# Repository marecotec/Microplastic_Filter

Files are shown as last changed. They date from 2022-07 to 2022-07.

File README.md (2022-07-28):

# URI Microplastic Pump-Filter System

The URI pump-filter system has been developed to improve our sampling volume for small plastic particles (down to 10 μm in size) whilst reducing contamination risk both before, during and after sampling. Field sampling methodologies for microplastics have been rapidly developing over recent years, however, many studies still rely solely on trawling surface waters using Manta Trawl systems, or sample only small volumes. This has led to limitations in the number of studies that sample microplastics at lower size fractions and the detectability of such particles.

Our system is a modification of the design published by [Lenz and Labrenz (2018)](https://www.mdpi.com/2073-4441/10/8/1055), but includes an alternative gradient filtration approach that allows for size fractionation of our samples at the point of collection. This also serves to increase sample volume throughout the sampled size range, and eases analyses in the laboratory.

The links below (and this repository) capture the general items needed if you would like to replicate such a system, we include photographs, methodologies and bill of materials to help you create your own system.

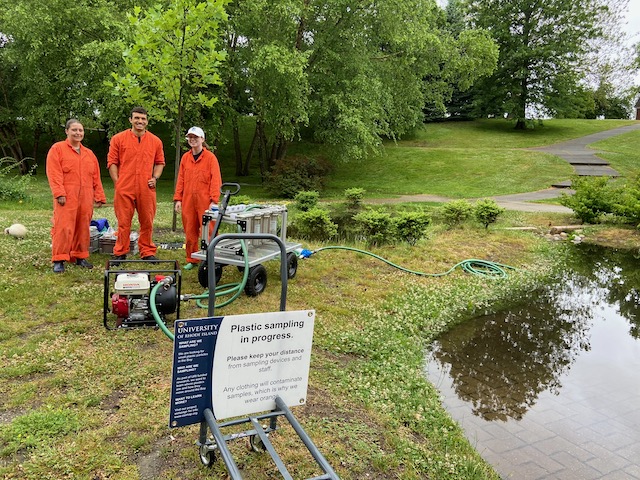
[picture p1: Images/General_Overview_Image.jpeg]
General overview of our team sampling in Roger Williams Park, RI


*General overview of our team sampling with the pump-filter in Roger Williams Park, RI in 2022*

## Table of Contents
[Technical Description](TECHNICALDESCRIPTION.md) - Description of the system.

[Technical Verification](TECHNICALVERIFICATION.md) - Methods used to test the system.

[Field Methods](FIELDMETHODS.md) - Methods used to collect samples from the field.

[Build log and bill of materials](BUILDLOG.md) - Build log and photos of the system, including bill of materials.

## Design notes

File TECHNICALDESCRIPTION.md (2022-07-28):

# Technical Description

The system is constructed from fully stainless steel (SS 316) 0.75 inch pipe and fittings mounted on an aluminum frame with 3D printed mounting parts constructed from PETG plastic. Pumping power is provided by a Honda WXT15 or a WMP20X gas pump for remote field operations. The basic system consists of two L-valves that allow us to change the directionality of water flow to allow for three functions, “sampling”, “cleaning” and “filter load/unload”. These functions are critical for effective sampling that limits potential contamination of our samples from our clothing and other airborne contaminants. No plastic parts are in contact with our sampled water (with the exception of the intake sampling hose; green PVC). The pump and flow meter are both situated behind the filter line, with the pump in a suction mode. Whilst suction is a less efficient pumping approach, it removes any potential sources of contamination from mechanically abraded parts, such as the pump impeller. Additionally, the seals on valves and cartridge filters are a rubber form. We can change or select filter sizes for specific situations but have established a size fractionation range of 280μm, 100μm and 10μm in series. Flow rate and volume are monitored using a domestic water flow meter commonly used to record freshwater flow, it provides accurate readings to +/- 1% of total volumetric flow.

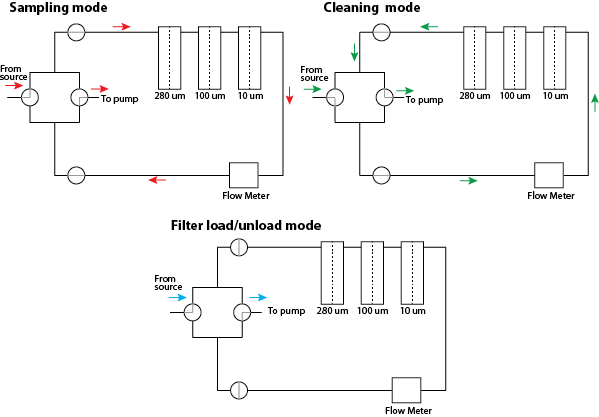
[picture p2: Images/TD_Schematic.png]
Schematic of the pump-filter system


*Schematic of the pump-filter system under different functional modes, including sampling, cleaning and filter load/unload. Valves are illustrated with the grey line(s) in a circle, and includes two valve types, straight and L.*

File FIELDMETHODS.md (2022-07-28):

# Field methodologies

We have undertaken repeated trials to establish strong field sampling protocols that are effective, efficient and repeatable under a variety of different situations. Our validated methodology is briefly as follows: Upon arrival at the sample site, precaution signs are placed to reduce any risk of contamination from bystanders and to ensure current social distancing rules are followed. To reduce contamination and to create identifiable contamination from team members, we all wear the bright orange, 100% cotton field gear (including COVID-19 compliant facial coverings). This allows us to discount orange fiber pollution, as bright orange pigments are rare in our samples anyway, from our analyses.

Before undertaking sampling, data on site water temperature, wind speed/direction, current speed/direction, weather conditions and tide are recorded. A wide-mouth mason jar filled with 100 ml of ultra-pure water (Milli-Q) is used as an air control and is opened to the surrounding air anytime the filter cartridges or sample jars are exposed to air to capture any potential levels of contamination during processing. Once sampling is started, the three filters are removed from their clean storage jars and mounted within the filter housings on the system in the correct order. To reduce any potential contamination, the system is first cleaned with a backflow (“Cleaning mode”) wash of 1 μm filtered water using a 1 μm filter mounted on the pump-filter system frame. We then take a control sample by running in “sampling mode” (Figure) using 1μm filtered water. This control provides a procedural control to ensure the system is clean and viable for sampling, our expectation is that there should be no or very minimal contamination within the system.

The 3 filter cartridges are then switched out of the system (stored in glass jars) for clean filters. Any water found in the filter housings that held the filters is also stored poured in a glass jar so it can be processed along with the filter. The system is then ready for seawater sampling (“Sampling mode”). We are still working to define our total sampling volumes, but our trials have so far shown that we can often pump 20-50 gallons, depending on site conditions (i.e., amount of organic or sediments in the water column), before the filters become blocked and pumping rate falls to zero. To continue pumping if we do not reach the target volume, we remove the smallest filter size (10 μm), and replace that with a fresh clean filter (both filters are processed in the laboratory). This allows us to pump over 50 gallons to collect a high volume sample that is size fractionated into our major size classifications, > 280 μm, 280-100 μm and  100-10 μm. Once filtering is finished, all filters and water within the filter housings are removed and stored in glass jars for transport to the laboratory. The system is then washed with fresh water and dried to prevent rust.

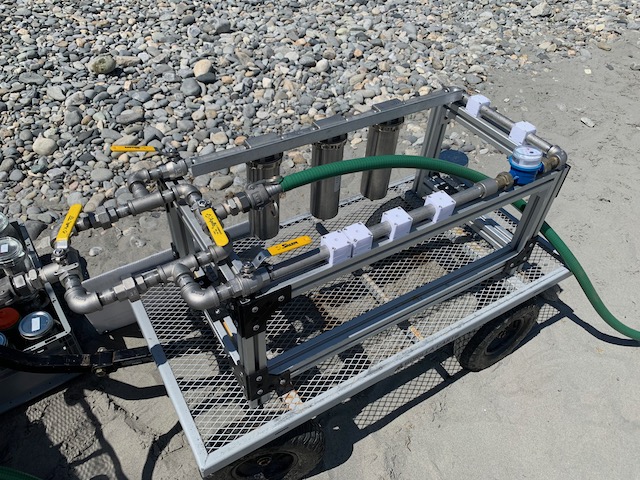
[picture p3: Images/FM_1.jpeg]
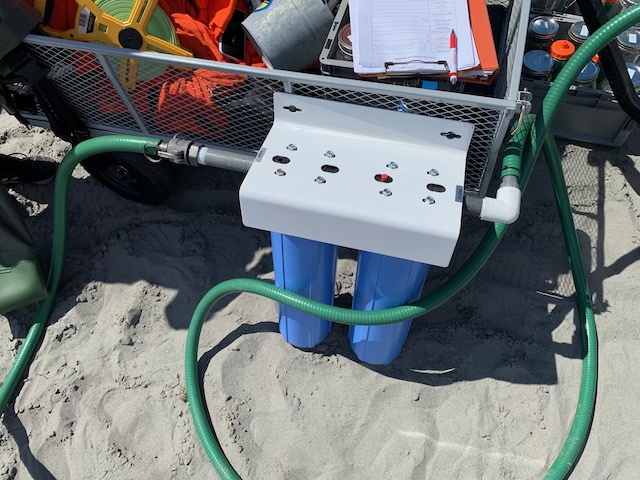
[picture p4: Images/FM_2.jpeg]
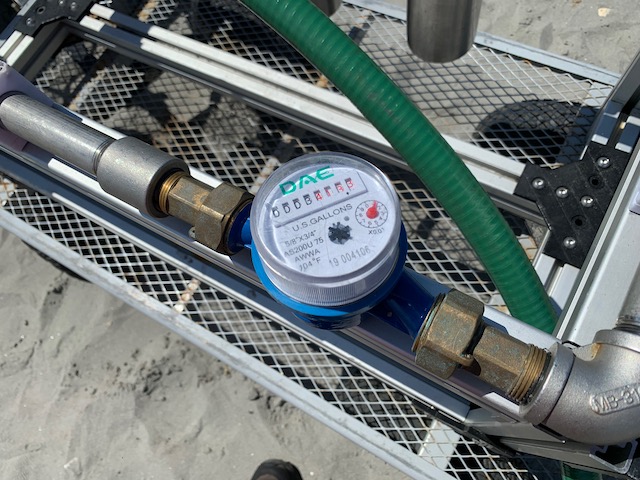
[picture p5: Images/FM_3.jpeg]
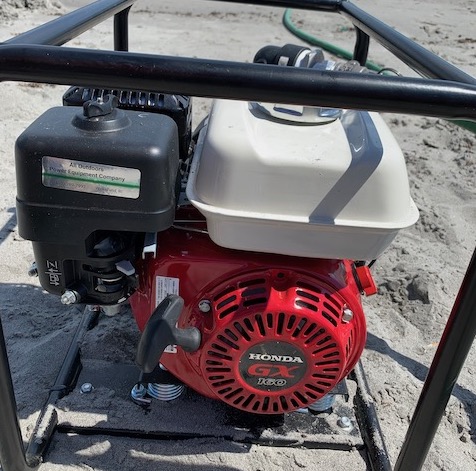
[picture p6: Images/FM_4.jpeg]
   

**The full operating procedure for the verification of the system can be found [here](Protocols/SOP_Pump-filter_field_sampling.pdf)**

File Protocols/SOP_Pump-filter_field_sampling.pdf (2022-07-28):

# Standard Operating Procedure for field sampling with the Pump-Filter System

by Brian Preziosi, Rory Maynard-Dean, Jacquline Roush, and Cara Megill Last updated Jan 22nd 2022

I. Materials
1. Per replicate (control and sample)
a. 6 - 64 oz. mason jars labeled with white electrical tape
b. 1 - 64 oz. mason jars filled with pure water
c. 6 - 32 oz. Gatorade squeeze bottles filled with pure water
d. 6 - Spaghetti jars each containing their respective filters (280 µm, 100 µm, 10 µm)
e. 1 – 32 oz mason jar (wide mouth) with 100 ml pure water in it to serve as an air control
2. Flathead screwdriver for prying open the filter housing
3. 5.5 qt metal bucket for catching spill when removing filter cartridge
4. 2 squeeze bottles filled with pure water (one with small tip and another with a cut tip)
5. 1 funnel for priming gas pump
6. At least 2 of the 1 µm filter cartridge (polypropylene string wound, 10” x 2.5”, from Amazon) (https://www.amazon.com/Aquaboon-Replacement-Compatible-SWC-25-1001-SWF-25-1001/dp/B01LY0VD79)
7. Filter pump system
8. 4 accompanying hoses:
a. Intake hose (reinforced hose with 1 wide attachment end and 1 threaded end)
b. Backwash filter hose (short reinforced hose)
c. Filter to pump hose (longer reinforced hose)
d. Outflow hose (normal gauge, non-reinforced hose)
9. WD-40
10. University truck
11. 1 HaulMaster 2-in-1 hand cart
12. 1 guerilla cart
13. 2 gas pumps
14. 1 boat hook to attaching to intake hose end so it can be held outwards in the water
15. 1 white buoy attached to wire to keep hose from sinking too far below the surface
16. 1 pair of waders
17. Orange cotton jumpsuits for all personnel
18. Waterproof paper + writing utensils
19. First Aid Kit

This filtration device was designed to eliminate sample contamination from outside microplastics either due to airborne particles or from usage-related wear of the materials (Lenz & Labrenz, 2018). The pump-filter system consists of a closed filter design and non-plastic materials in order to achieve this.
The pump filter system utilizes suction to pull water in and through the filter apparatus first before going to a gas pump. This ensures none of the sample gets ground up by the gas pump. A green intake hose, with one quick-release fitting and an open-end, is connected to the intake valve, from here water is flushed through the system to the outflow valve. The intake hose has a 4 mm metal strainer attachment fitted to the open end in order to prevent clogging and intake of large debris. Another green hose, fitted with quick-release fittings on both ends, connects the outflow of the filter apparatus to the intake of the gas pump. Suction from this pump is what ultimately draws water into the system and through the filter cartridges. Water then exits the system through a third green hose connected to the outflow pipe at the top of the gas pump and is returned to the environment.

II. Gathering Materials
1. Use the hand cart to load all the materials from into the back of the truck, this includes all the jars, squeeze bottles, bottles, waders, 5.5 Qt bucket and tools. Remember to place 2 Gatorade squeeze bottle in each grey, plastic box of 6 jars to keep the jars from clanking against each other during transport as seen in figure 1.
2. At the loading dock of the Center for Biotechnology and Life Sciences, get the intake hose (if it was left on pump) and gas pump from outside cage (key is on top of metal shelves just inside building). Take the gas can as well. Load both gas pumps and the gas can onto the back of the truck.
3. At the Furtado warehouse on Bay Campus, load the pump filter system onto the guerilla cart and load both onto the back of the truck. Remember to also take the boat hook (long metal pole) and white buoy from Furtado.

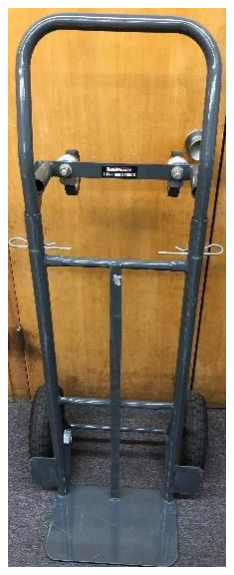
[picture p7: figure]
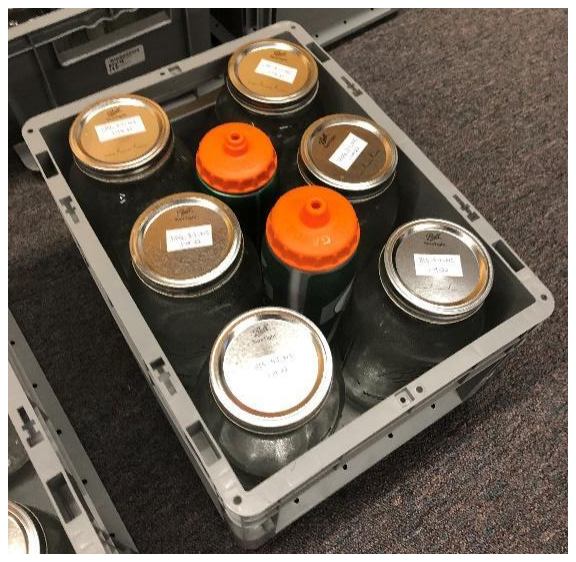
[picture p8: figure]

Figure 1. The picture at the left is of the HaulMaster 2 in 1 handcart in the vertical configuration. If needed, it can be switched to the horizontal configuration be removing the silver loops inserted in the outside of the mid portion of the cart so the handle can be moved to the other set of holes. The picture on the right shows where to insert the 2 Gatorade squeeze bottles into each box of 64 oz jars so that all jars become tightly packed. The same layout can be used with spaghetti jars.

III. Setting Up the System at the Site
1. Put on the orange jumpsuits.
2. Remove all grey boxes with jars to be used at the site, the toolbox, and the guerilla cart from the back of the truck.
3. Load the pump frame onto the guerilla cart and pull it to the water’s edge. Take the filter system frame off the cart. Keep all grey boxes with required jars nearby.
4. Attach hoses as seen in figure 2. Make sure the hose going to the 1 µm filter is part of the flow loop so all water gets filtered first as it goes into system.
5. Attach the boat hook end and buoy are to the end of the intake hose as seen in left picture of figure 7 if this has not already been done.

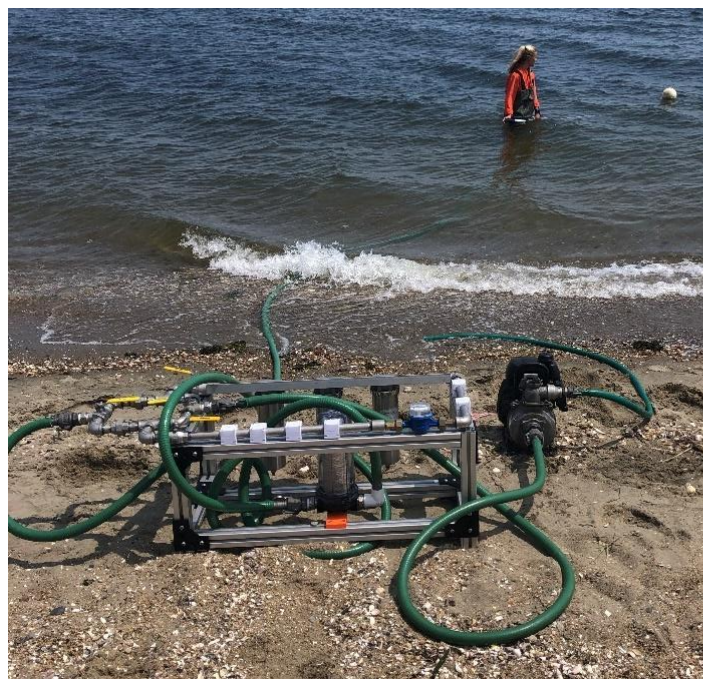
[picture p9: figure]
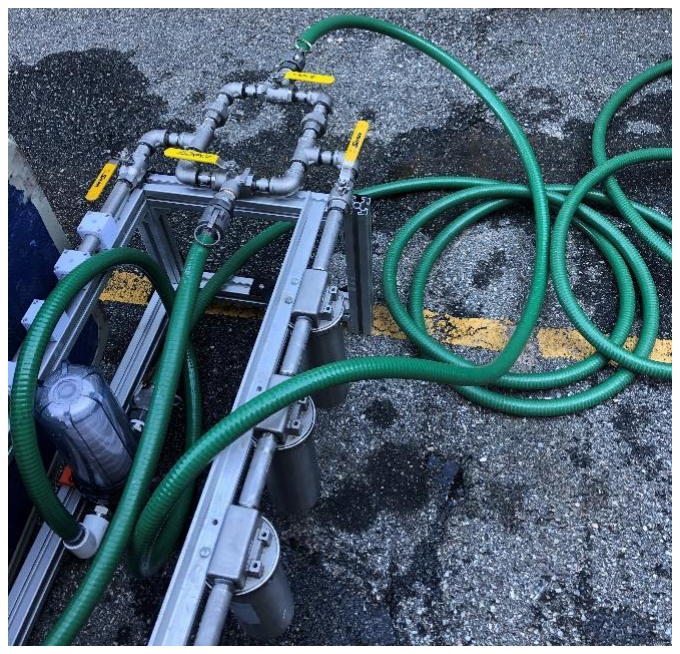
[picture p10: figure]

Figure 2. Hose set-up for backflow and forward control pump (goes through 1 µm filter). Note that the only difference between backflow and forward control pump configurations is the way the valves are turned, hose configuration remains the same. Valves are set to backflow configuration on the left picture and the valves are set to forward control pump configuration in the right picture. The intake hose connects to the right-hand side of the 1 µm filter cartridge and the hose on the left-hand side of the 1 µm filter cartridge then connects to the opening at the north of the steel frame. The water then travels through the frame and steel filters and comes out the hose attached pointing south (towards inside of steel frame). That hose then leads to the pump which then moves the water out another hose attached to the pump. Field location in right picture is Spink Neck beach and the person holding the boat hook in the water is Morgan McCutcheon.
IV. Backflow
1. Change valves to the positions seen in figure 3.
2. Prime the gas pump with water from the metal tub using on the 5.5 qt buckets. Water will go in the top of the gas pump, unscrew the opening to access.
3. Take note of where flowmeter starts.
4. Have one person put the waders on and walk out into the water to about waist height (3-4 foot water depth) with the boat hook in hand with the buoy and intake hose attached. Hold hook 1.5-2 feet below water surface but well above the sediment at the bottom. Record depth of water and hose position (post collection), state of tide and estimate distance from shore (think about a relatable part of the shore to account for variable tides).
5. Start the gas pump and set it to 100% full throttle (as shown in figure 4).
6. Allow pumping to continue for 15 gallons, flowmeter will count down so stop flow 15 gallons from the starting reading.
7. Turn the 2 side valves off at the same time and then turn the center valve.

8. Turn off the gas pump.

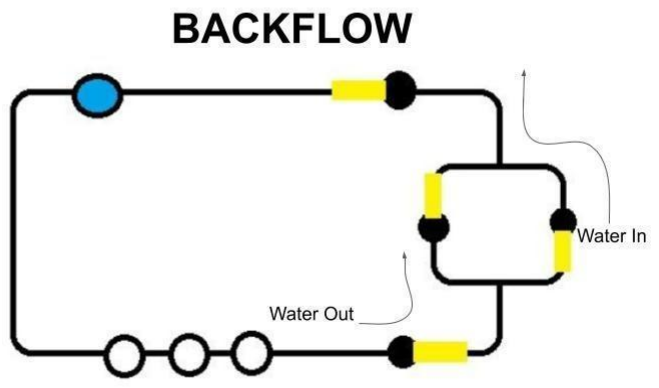
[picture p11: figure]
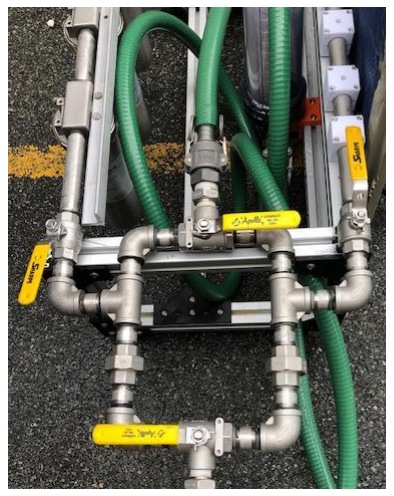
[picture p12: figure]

Figure 3. Backflow valve positions. Diagram credit: Jacquline Roush.

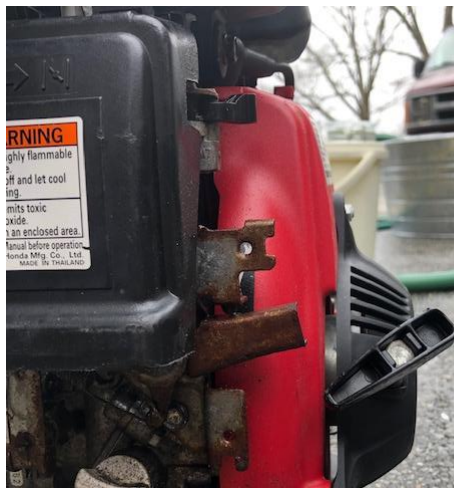
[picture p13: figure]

Figure 4. Throttle (longest metal lever) of gas pump set to 100% power for use with backflow pumping.

V. Control Forward Pump
1. Load the control cartridge filters
2. Make sure boat hook end and buoy are attached to the end of the intake hose as seen in left picture of figure 7.
3. Take note of where flowmeter starts.
4. If they are not already out there, have one person put the waders on and walk out into the water to about waist height (3-4 foot water depth) with the boat hook in hand with the buoy and intake hose attached. Hold hook 1.5-2 feet below water surface but well above the sediment at the bottom. Record depth of water and hose position (post collection), state of tide and estimate distance from shore.
5. Switch the valves to forward flow as seen in figure 5.
6. Switch gas pump to 75% throttle as seen in figure 6.
7. Turn the gas pump on and allow it to run for 50 gallons.
8. Turn both side valves off then turn the middle valve.
9. Turn off the gas pump.
10. Place the 5.5 qt bucket under the 280 µm cartridge filter canister.
11. Remove the 280 µm filter cartridge by unscrewing the canister ring at the top and wedging the screwdriver in the opening as seen on the right-hand side of figure 7. Turn the screwdriver slowly to pry the suction seal open.
12. Place the filter cartridge in the appropriately labeled spaghetti jar
13. Pour the canister water in the appropriately labeled 64 oz mason jar.
14. Rinse the sides of the canister with a 32 oz (946 ml) Gatorade squeeze bottle until the water level is just below the top of the metal spring at the bottom of the canister. Swirl this water and pour out the side of the canister with the label on it. Repeat this 4 times and start pouring water into the spaghetti jar when the mason jar fills up.
15. Hold the canister upside down over the spaghetti jar and use 250 mL from sniped tip squeeze bottle to rinse contents from bottom of canister into spaghetti jar.
16. Rinse the O-ring and area canister was attached to using the sniped tip squeeze bottle into the bucket below. Then rinse the bucket contents into the spaghetti jar using the sniped tip squeeze bottle.
17. Load the 280 µm filter cartridge for the forward pump into the canister and load the canister back into the metal frame. This is best done with one person pushing the frame down while the other pushes the canister up.
18. Repeat steps 10 through 17 for the 100 µm and 10 µm filter cartridges.

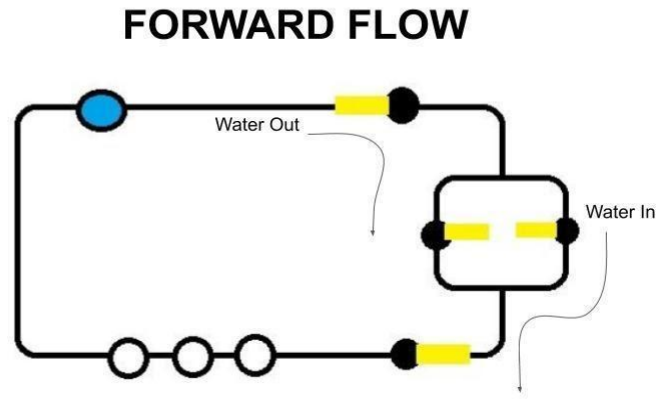
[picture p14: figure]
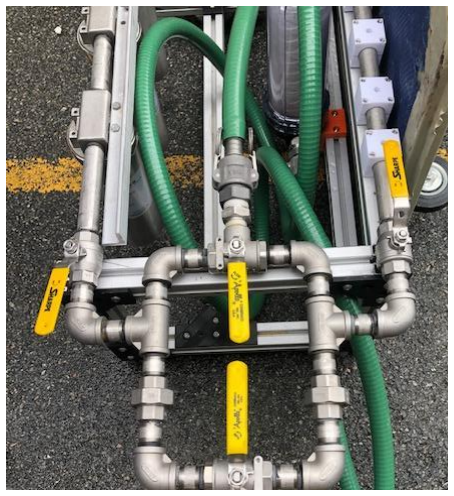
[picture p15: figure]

Figure 5. Forward pump valve positions. Diagram credit: Jacquline Roush.

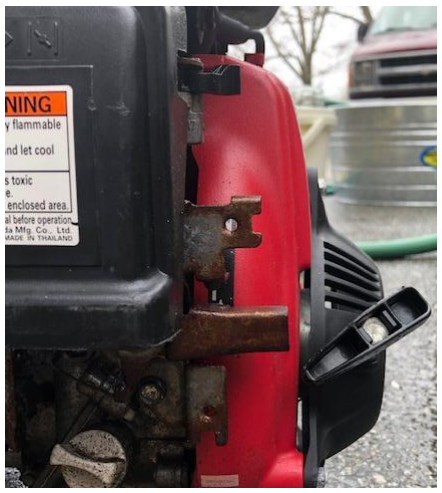
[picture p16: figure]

Figure 6. Throttle (longest metal lever) of gas pump set to 75% power for use with all forward flow pump runs.

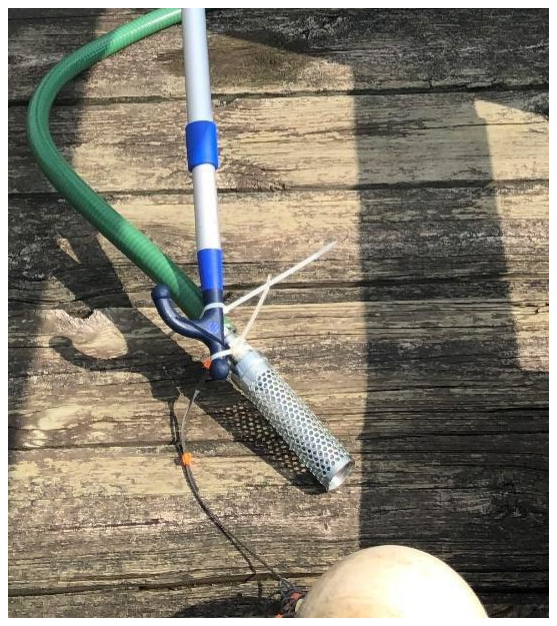
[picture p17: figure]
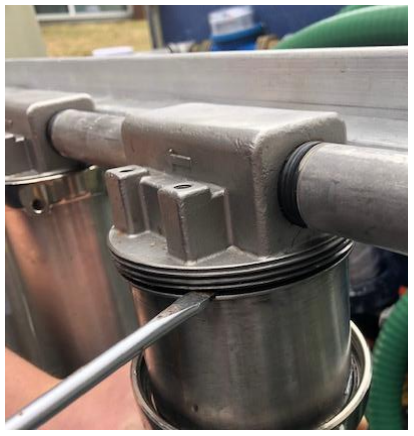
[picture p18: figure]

Figure 7. Picture on the left shows the boat hook and buoy attached to the intake end of the hose. Picture on the right shows where to wedge the flathead screwdriver above the canister holding the filter cartridge so suction pressure can be gently released.

VI. Environmental Forward Pump
1. Switch hoses so water no longer goes through the 1 µm filter loaded on the frame as seen in figure 8.
2. Turn on the gas pump with throttle still at 75%.
3. Take note of where flowmeter starts and wait until flow meter starts moving.
4. Make sure the person standing in the water with intake hose is still holding the hose above the sediment.
5. Have the other person start the gas pump once the intake hose is being held constant in place by the person out in the water.
6. Allow pumping to continue for 50 gallons.
7. Turn both side valves off and then turn the center valve.
8. Turn off the gas switch on the gas pump and allow it to run until it burns leftover gas in the main compartment out.
9. Repeat steps 10 through 16 from the above “Control Forward Pump” section for each of the 3 canisters to collect sample.

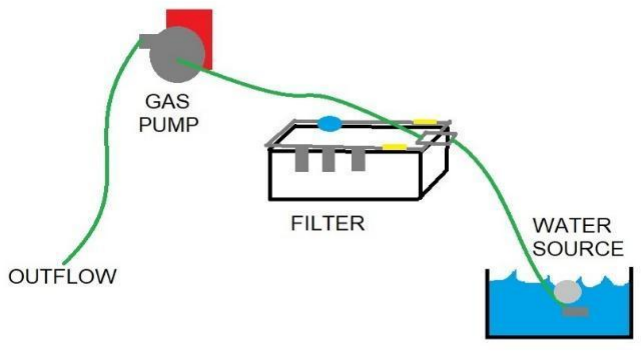
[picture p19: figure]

Figure 8. Pump filter set-up with hose connections made to direct water from the environment, through the metal frame with the steel filters, through the gas pump, and then out the outflow hose. The 1 µm filter is left out of this flow loop as the hose attached to one end of it just goes to the other end of the filter. Diagram credit: Jacquline Roush.
VII. Clean Up
1. Disconnect all hoses.
2. Tip the system forward and open valves to drain water out.
3. Open drain at bottom of gas pump and till it forward to drain it.
4. Lift the pump frame onto the guerilla cart.
5. Load all materials onto the back of the truck and travel to next site or URI Bay Campus when done for the day.
6. If done for the day, use the fresh water hose near Furtado to rinse out the inside and outside of the pump filter system frame. Rinse out inside of the gas pump only (do not spray outside).
7. Coil and tie all green hoses place all of them except the intake hose between the pump frame.
8. Spray gas pump with WD-40
9. Put the green intake hose and the gas pump back in the metal cage.

References

Lenz, R., Labrenz, M. Small Microplastic Sampling in Water: Development of an Encapsulated Filtration Device. Water. 2018, 10: 1-8.

Site Data Sheet

Site Name/Number

Collector(s) Name:

Date/Time | Date: Time:
GPS Location | Long: Lat:

Tide Height

General Weather Conditions

Substrate Type

Wind Speed/Direction | Speed: Direction:

Water Temperature

Salinity

Flow Meter Reading | Start of Backflushing: End of Backflushing: End of Forward Flush (CON.): End of Forward Flush (ENV.):

Total Amount of Water Sampled (gallons)

Current Speed/Direction | Speed: Direction:

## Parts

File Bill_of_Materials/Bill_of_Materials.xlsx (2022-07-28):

Item Number | Name | Part ID | Supplier | Dimensions | Quantity | Link | Notes
Frame Construction
1 | T-Slotted Framing, 45 mm square, hollow | 5537T915 | McMaster | 42 inches L | 3 | Link (https://www.mcmaster.com/catalog/128/2108/)
2 | T-Slotted Framing, 45 mm square, hollow | 5537T915 | McMaster | 15 inches | 8 | Link (https://www.mcmaster.com/catalog/128/2108/)
3 | T-Slotted Framing, corner bracket | 5537T938 | McMaster | NA | 14 | Link (https://www.mcmaster.com/5537T938/) | Can be subsituted or complimented with 3D printed brackets
4 | Tee nut M8 | 5537T688 | McMaster | NA | 50 |  | 50 approximately required
5 | M8 Socket head screw
6 | Marine-Grade 5086 Aluminum 90 Degree Angle | 4039T16 | McMaster | 3 foot L, 1.25 height | 1 | Link (https://www.mcmaster.com/4039T16/)
Pipe and valves
7 | Threaded diverting valve | 4467K44 | McMaster | NA | 2 | Link (https://www.mcmaster.com/4467K44/)
8 | Ultra-Corrosion Resistant Full-Port On/Off Valve | 46495K22 | McMaster | NA | 2 | Link (https://www.mcmaster.com/46495K22/)
9 | Standard-Wall 316/316L Stainless Steel Pipe | 4816K191 | McMaster | 14 inches | 1 | Link (https://www.mcmaster.com/4816K191/)
10 | Standard-Wall 316/316L Stainless Steel Pipe | 4816K194 | McMaster | 22 inches | 1 | Link (https://www.mcmaster.com/4816K194/)
11 | Standard-Wall 316/316L Stainless Steel Pipe | 4548K193 | McMaster | 2 inches | 12 | Link (https://www.mcmaster.com/4548K193/)
12 | Standard-Wall 316/316L Stainless Steel Pipe | 4548K197 | McMaster | 5 inches | 3 | Link (https://www.mcmaster.com/4548K197/)
13 | Standard-Wall 316/316L Stainless Steel Pipe | 4548K345 | McMaster | 6.5 inches | 1 | Link (https://www.mcmaster.com/4548K345/)
14 | Standard-Wall 316/316L Stainless Steel Pipe | 4452K115 | McMaster | Connector | 1 | Link (https://www.mcmaster.com/4452K115/)
15 | Standard-Wall 316/316L Stainless Steel Pipe | 4548K198 | McMaster | 6 inches | 1 | Link (https://www.mcmaster.com/4548K198/)
16 | 316 Stainless Steel Threaded Pipe Fitting - Tee | 4452K435 | McMaster |  | 2 | Link (https://www.mcmaster.com/4452K435/)
17 | 316 Stainless Steel Threaded Pipe Fitting - Elbow | 4452K415 | McMaster |  | 8 | Link (https://www.mcmaster.com/4452K415/)
Filters and filter housings
18 | 280 um stainless steel cartridge | 10C316-SC280-C98B0B | Serv-A-Pure | 9.875" | 1 | Link (https://www.servapure.com/Stainless-Steel-Cylindrical-Cartridge-316-SS-10-Inch-Length_p_11586.html) | Only need one for the system, but if doing multiple sites, need to increase
19 | 100 um stainless steel cartridge | 10C316-SC100-C98B0B | Serv-A-Pure | 9.875" | 1 | Link | Only need one for the system, but if doing multiple sites, need to increase
20 | 10 um stainless steel cartridge | 10C316-SC10-C98B0B | Serv-A-Pure | 9.875" | 1 | Link
21 | Quantrol QFP1X10-3/4 | QFP1X10-3/4 | Serv-A-Pure | 10 inch | 3 | Link (https://www.servapure.com/Quantrol-QFP1X10-34-10-316SS-Single-Cartridge-Filter-Housing-_p_9770.html)
Control filters
22 | Pentek Big Blue Water Filtration System | BBFS-22 | Serv-A-Pure | 20 inch | 1 | Link (https://www.servapure.com/Pentek-BBFS-22-Two-Big-Blue-Housing-Water-Filtration-System-160166_p_1926.html)
23 | Big Blue Filter, 25/1 Micron | 155360-43 | Serv-A-Pure | 20 inch | 1 | Link (https://www.servapure.com/Pentek-155360-43-DGD-2501-20-45-x-20-Big-Blue-Filter-251-Micron_p_1594.html)
24 | Big Blue Filter, 75/25 Micron | 155356-43 | Serv-A-Pure | 20 inch | 1 | Link (https://www.servapure.com/Pentek-155356-43-DGD-7525-20-45-x-20-Big-Blue-Filter-7525-Micron_p_1592.html)
Hose and fittings
 | Suction Water Hose, 1" ID, 1-5/16" OD | 5293K38 | McMaster | 50 foot | 1 | Link (https://www.mcmaster.com/5293K38/)
 | Anodized Aluminum Cam-And-Groove Hose Coupling, Size 1, Socket With Nonlocking Levers, 1" Hose Id | 2084T32 | McMaster | NA | 3 | Link (https://www.mcmaster.com/catalog/2084T32)

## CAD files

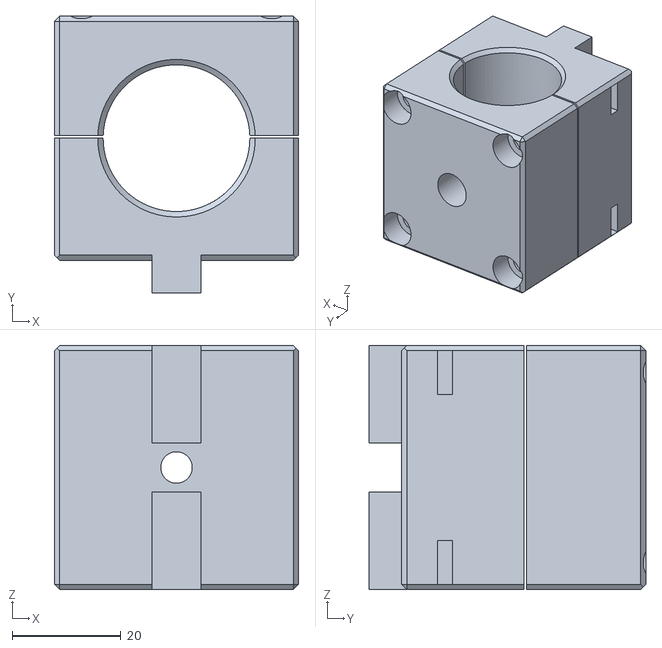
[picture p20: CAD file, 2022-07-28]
3D_Printed_Parts/Pump System Clamp.stl
45.0 x 51.0 x 45.0

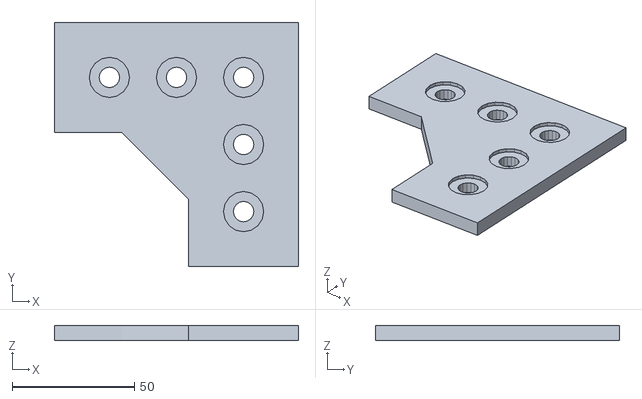
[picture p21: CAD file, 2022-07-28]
3D_Printed_Parts/Pump_System_Extrusion_Bracket_4545.stl
100.0 x 100.0 x 6.00

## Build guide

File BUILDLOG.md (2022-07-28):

# Build log and bill of materials

Constructing a system similar to the *URI Microplastic Pump-Filter System* is a fairly simple process providing you have access to the tools required. All the components bar a few 3D printed parts can be purchased off the shelf following the [Bill of Materials](Bill_of_Materials.xlsx). The system needs a moderately powered gas (or electrical pump if you have power) pump to operate, and we maintain two Honda Pumps (WX15T and WMP20X). Pump selection is exceptionally context specific and will need to be investigated depending on several factors.

## Tools used

- 3D printer
- 2 x pipe wrenches
- Adjustable wrenches
- Electrical drill
- Drill bits of associated sizes
- Cheater bar

## Building

First, acquire all parts and 3D print parts needed (extrusion angle brackets and the main tube system holder). Assemble all the 0.75 inch stainless pipe and the extrusion. Ensure all joints are sealed with either thread tape or pipe dope and are adequately tightened to avoid leaks (leaks will reduce the pump efficiency and impact your readings on the flow meter).

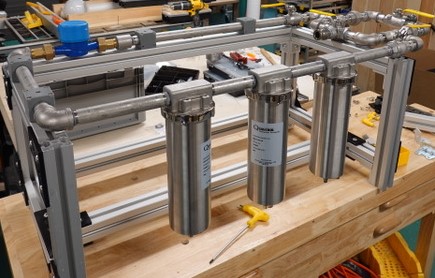
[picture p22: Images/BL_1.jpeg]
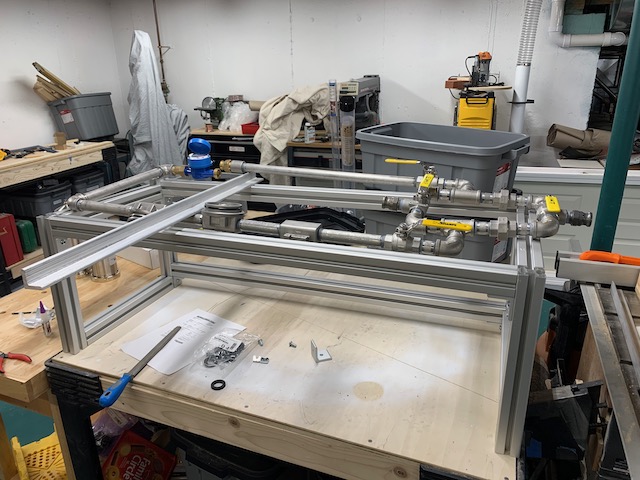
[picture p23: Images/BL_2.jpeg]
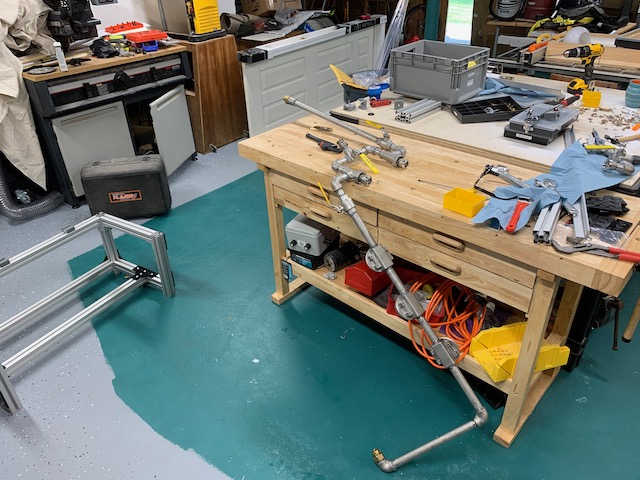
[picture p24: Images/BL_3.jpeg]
  

General steps:
1. Assemble frame the frame construction.
2. Plumb in the filter housings. This can be tricky to get them all in near vertical alignment and you may need to add signifcant torque to get the housings to align.
3. Prepare the aluminum angle support bar to hold the filter housings together, drill as appropriate to take the bolts for the top of the housings.
4. Mount all 3D printed pipe clamp halves, and then attach the tops to secure the frame to the system.

## 3D printed parts

We printed our 3D printed parts with a high infill for strength and used PETG filament on a Prusa i3 MK3S.

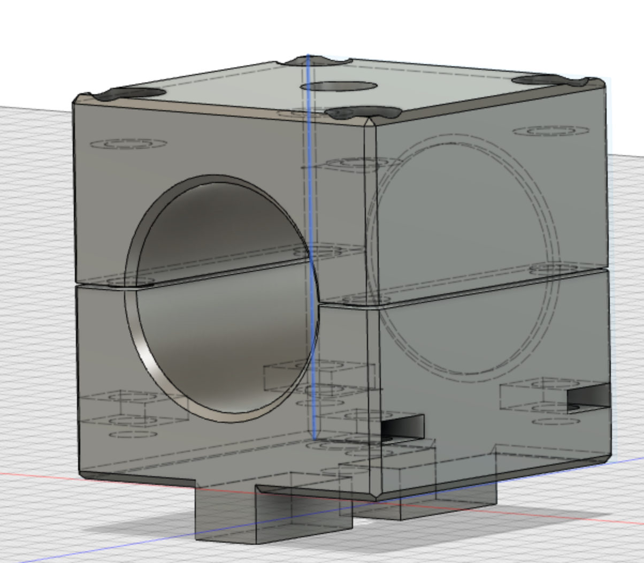
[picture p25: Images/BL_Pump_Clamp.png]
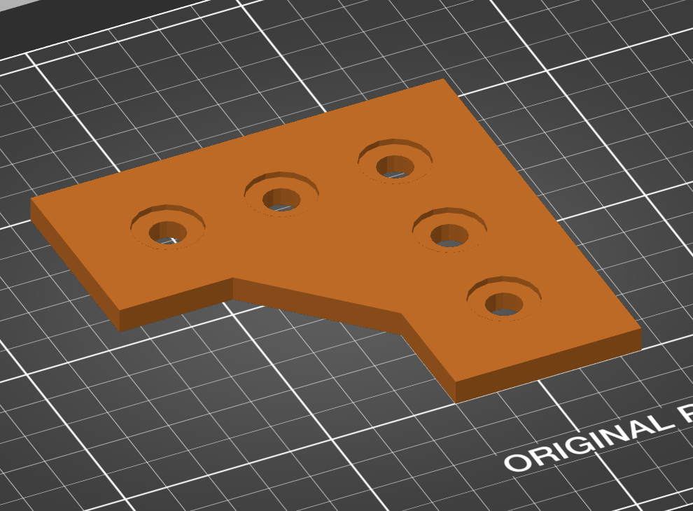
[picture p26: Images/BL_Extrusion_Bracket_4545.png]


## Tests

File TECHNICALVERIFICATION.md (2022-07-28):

# Technical verification

We have undertaken a series of plastic and fiber recovery trials to test the pump-filter system and the methodology described above. In Lenz and Labrenz (2018), cylindrical plastic particles (polyamide) with a length of 450 μm and a diameter of 480 μm were seeded within their system, with a recovery rate of 98.9%. We conducted similar methodological trials, however, we used a range of particle sizes and types in an attempt to stress test the system. This exhaustive testing allowed us to develop a standard operating procedure for operating the pump-filter system as well as extracting samples from the filters once they are taken out of the pump-filter system. Our basic seeding protocol utilized 3 different sizes of polyethylene fluorescent beads with sizes of 355-425 μm, 150-180 μm, and 15 μm, as well as polyester fibers (width of 17-20 μm, length of 658-675 μm). To conduct each trial we counted about 100 of each size and type and seeded these into the intake of the pump-filter system.

During conducting numerous trials (approximately 30 in total), many improvements were made to the extraction procedure to bolster fiber and bead recovery rates. We found that sonication of the filter cartridges is necessary to obtain recovery rates of 94% or better since washes with squeeze bottles alone do not remove all particles and fibers entrained on the filter mesh. Standardized methodologies and high levels of training and practice are also needed to ensure repeatable extraction protocols that were consistent between trials and users.

Below are a series of results from one of our later trials that ultimately drove the adoption of our field methodologies. This included an additional step was the washing of the bottom of the canisters used to house the filter cartridges within the pump-filter system a total of 5 times to dislodge any portion of the sample stuck under the spring located at the bottom of the canister. The use of a flathead screwdriver to gently break the suction seal between the canister holding the filter cartridge and the system frame was also found to help reduce splashing of the water in the canister out of the sample. Any water that does splash out is caught in a metal bucket placed just below the canister. Tracking down missing beads after each of the pilot recovery trials helped determine these improvements were needed and allowed for refinement of the method. We achieved between 94.2% and 100% recovery rate for our different particle sizes and types and obtained 100% average recovery of our 355-425 µm beads, exceeding the results Lenz and Labrenz (2018) obtained with their 480 μm diameter polyamide particles.

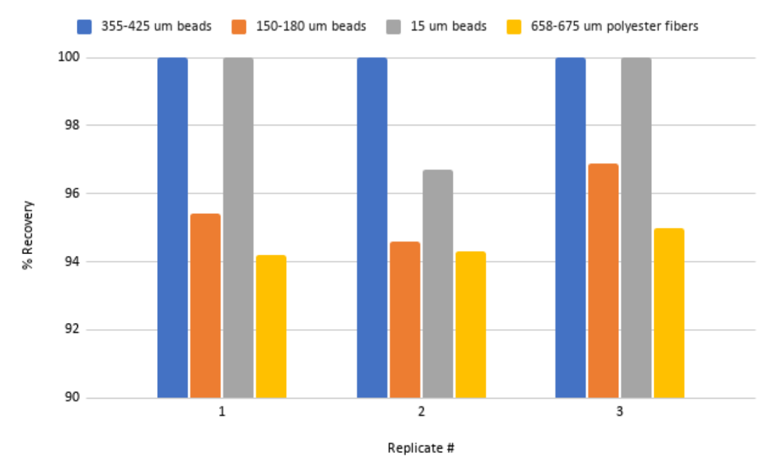
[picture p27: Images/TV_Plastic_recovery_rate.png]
Recovery rate graph


|           | Beads      | Beads      | Beads     | Fibers    |
| --------- | ---------- | ---------- |---------- |---------- |
| Replicate | 355-425 μm | 150-180 μm | 15 μm | 658-675 μm |
| 1         | 100        | 95.4       | 100 | 94.2 |
| 2         | 100        | 94.6       | 96.7 | 94.3 |
| 3         | 100        | 96.9       | 100 | 95 |
| Mean      | 100        | 95.6       | 98.9 | 94.5 |

*Validation trials of pump-filter seawater collection system using 3 sizes of fluorescent, polyethylene bead sizes in addition to polyester fibers. The number of fibers and beads used to seed the system ranged between 73 and 108 per particle type per replicate.*

**The full operating procedure for the verification of the system can be found [here](Protocols/SOP_Pump-filter_spike_test.pdf)**

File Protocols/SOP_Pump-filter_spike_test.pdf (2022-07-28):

Standard Operating Procedure for a Plastic Spike Test of the Pump-Filter System Contributors: Brian Preziosi, Rory Maynard-Dean, Sarah Davis
I. Materials
Per replicate (control and sample):
6 - 64 oz. mason jars labeled with white electrical tape (3 environmental, 3 control) 1 - 64 oz. mason jars filled with Milli-Q water
6 - 32 oz. gatorade squeeze bottles filled with Milli-Q water
6 - Spaghetti jars each containing their respective filters (280um, 100um, 10um) 28 gal. metal tub
300 um and 50 um sieve for outflow monitoring
Flathead screwdriver for prying open the filter housing
5.5 qt metal bucket for catching spill when removing filter cartridge
2 squeeze bottles filled with Milli-Q (one with small tip and another with a cut tip) Jar (4 oz. mason) containing pre-counted quantity of beads suspended in milli-Q water 2 funnels, 1 for priming gas pump and another for pouring beads through
Filter pump system
4 accompanying hoses:
Intake hose (reinforced hose with 1 wide attachment end and 1 threaded end) Backwash filter hose (short reinforced hose)
Filter to pump hose (longer reinforced hose)
Outflow hose (normal gauge, non-reinforced hose)
Gas powered pump
WD-40
2 clamps

II. Setting Up the System
1. Unpack all materials from metal tub upon arrival at field location.
2. Lift pump frame off the tan cart.
3. If windy, place the tan cart at the back side of the metal frame as seen in figure 1.
4. If at CBLS, get the black hose and faucet key (has square hole at tip), this is on a cart on your left as you go inside CBLS loading dock. Attach the black hose to the hydrant faucet just to the left of loading dock door.
5. Attach freshwater source hose to stand alone 1 um filter housing and turn on hose water to fill metal tub.
6. Attach hoses as seen in figure 1. Make sure the hose going to the 1 um filter is part of the flow loop so all water gets filtered first as it goes into system.

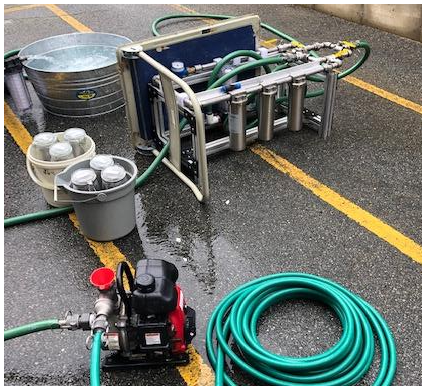
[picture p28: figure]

Figure 1. Pump filter set-up for with hose connections made to direct water from the metal tub, through the 1 um filter on the metal frame, through the metal frame, through the gas pump, and then out the outflow hose (coiled at bottom of picture).
III. Backflow
1. Change valves to positions in seen in figure 2.
2. Place the 300 um sieve at outflow hose and place outflow hose by the drain, have one person hold the outflow hose over the sieve.
3. Prime the gas pump with water from the metal tub using on the 5.5 qt buckets. Water will go in the top of the gas pump, unscrew the opening to access.
4. Start the gas pump and set it to 100% full throttle (as shown in figure 3).
5. Allow pumping to continue for 15 gallons, flowmeter will count down so stop flow 15 gallons from the starting reading.
6. Turn the 2 side valves off at the same time and then turn the center valve.
7. Turn off the gas pump.

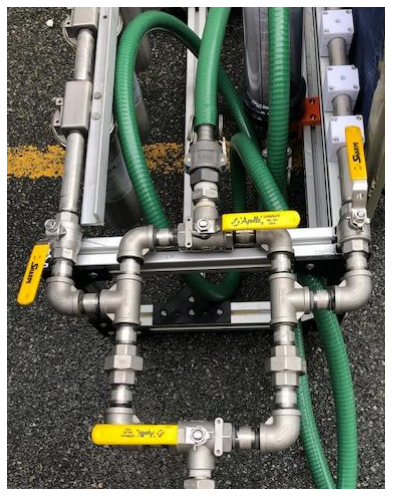
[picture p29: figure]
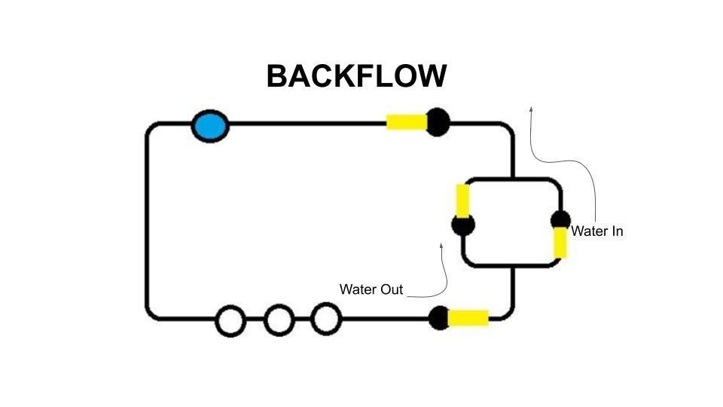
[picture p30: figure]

Figure 2. Backflow valve positions. Diagram credit: Jacquline Roush.

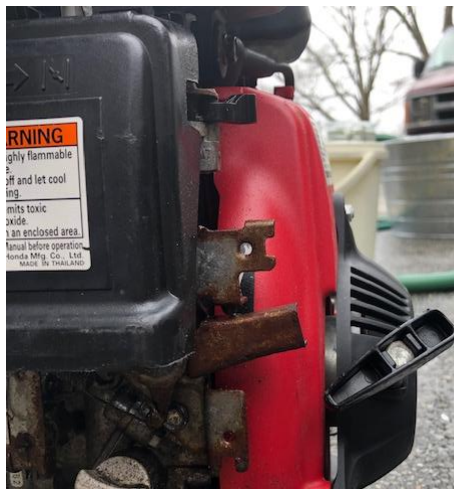
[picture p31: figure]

Figure 3. Throttle (longest metal lever) of gas pump set to 100% power for use with backflow pumping.
IV. Control Forward Pump
1. Load the control cartridge filters
2. Clamp the outflow hose to side of the metal tub so that it does not touch water.
3. Switch the valves to forward flow as seen in figure 4.
4. Switch gas pump to 75% throttle as seen in figure 5.
5. Clamp outflow hose to the side of the tub and place outflow hose near center of tub as seen in figure 6.
6. Turn the gas pump on and allow it to run for 40 gallons.

7. Turn both side valves off then turn the middle valve.
8. Turn off the gas pump.
9. Place the 5.5 qt bucket under the 280 um cartridge filter canister.
10. Remove the 280 um filter cartridge by unscrewing the canister ring at the top and wedging the screwdriver in the opening as seen on the right hand side of figure 6. Turn the screwdriver slowly to pry the suction seal open.
11. Place the filter cartridge in the appropriately labeled spaghetti jar
12. Pour the canister water in the appropriately labeled half gallon mason jar.
13. Rinse the sides canister with a 32 oz (946 ml) Gatorade squeeze bottle until the water level is just below the top of the metal spring at the bottom of the canister. Swirl this water and pour out the side of the canister with the label on it. Repeat this 4 times and start pouring water into the spaghetti jar when the mason jar fills up.
14. Hold the canister upside down over the spaghetti jar and use 250 mL from sniped tip squeeze bottle to rinse contents from bottom of canister into spaghetti jar.
15. Rinse the O-ring and area canister was attached to using the sniped tip squeeze bottle into the bucket below. Then rinse the bucket contents into the spaghetti jar using the sniped tip squeeze bottle.
16. Load the 280 um filter cartridge for the spiked forward pump into the canister and load the canister back into the metal frame. This is best done with one person pushing the frame down while the other pushes the canister up.
17. Repeat steps 8 through 15 for the 100 um and 10 um filter cartridges.

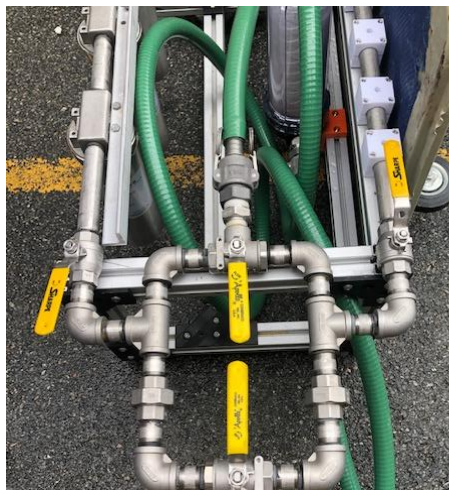
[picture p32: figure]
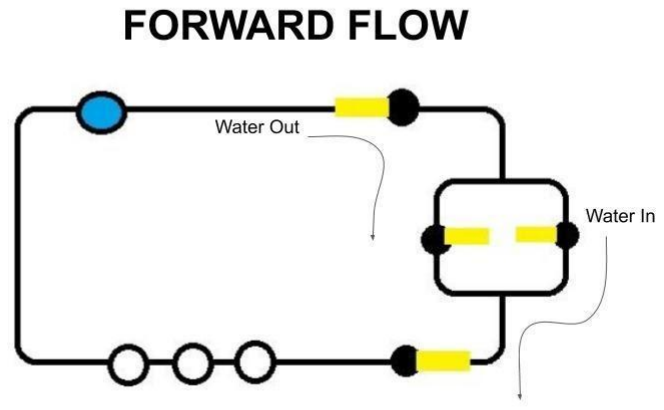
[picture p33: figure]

Figure 4. Forward pump valve positions. Diagram credit: Jacquline Roush.

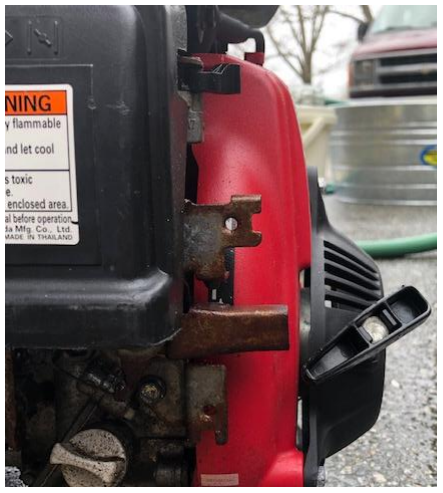
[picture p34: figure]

Figure 5. Throttle (longest metal lever) of gas pump set to 75% power for use with all forward flow pump runs

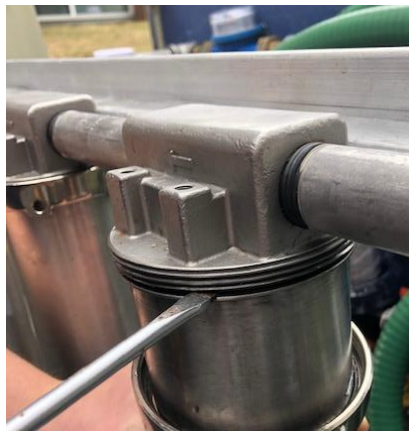
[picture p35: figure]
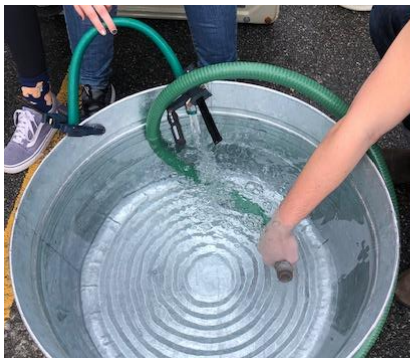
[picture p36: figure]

Figure 6. Picture on the left shows placement of intake hose near the center of the tub and the outflow hose clamped on side of tub pointing down to prevent circular current from forming for all forward flow pump cycles. The intake hose need only be held while beads are being fed into it during a spiked forward flow cycle. Picture on the right shows where to wedge the flathead screwdriver above canister holding the filter cartridge so suction pressure can be gently released.
V. Spiked Forward Pump

1. Switch hoses so water no longer goes through the 1 um filter loaded on the frame as seen in Figure 7.
2. Turn on the gas pump with throttle still at 75%.
3. Take note of where flowmeter starts and wait until flow meter starts moving.
4. Have one person hold the intake of the hose under the water in the metal tub with one hand and hold the plastic funnel just over the intake hose with the other. Make sure a whirlpool of suction was present over the hose before funnel was placed over it.
5. Pour beads from 4 oz. mason jar into the funnel, then rinse the inside of the jar 5 times using the sniped tip squeeze bottle. Rinse outside of jar as well. Use small tip squeeze bottle to rinse the rim of the jar and the lid. Inspect jar for any remaining beads.
6. Rinse the funnel with the sniped tip squeeze bottle.
7. Allow pumping to continue for 10 gallons then take the outflow hose and sieve out of the tub so water level of the tub begins to drain. Allow pumping to continue until all water is drained from tub. This should come to a total of 30 gallons of water pumped after the beads have been put in system.
8. Turn both side valves off and then turn the center valve.
9. Turn off the gas switch on the gas pump and allow it to run until it burns leftover gas in main compartment out.
10. Repeat steps 8 through 15 from the above “Control Forward Pump” section for each of the 3 canisters to collect sample.


Figure 7. Hose set-up for forward bead spike pump (does not go through 1 um filter).
VI. Clean Up
1. Disconnect all hoses but catch water that comes out with the 50 um sieve to check for any particles or fibers that got left in the system.
2. Tip the system forward and open valves to drain water out through the 50 um sieve.
3. Open drain at bottom of gas pump and till it forward to drain it into the 50 um sieve.
4. Lift the pump frame onto the tan cart.
5. Coil and tie all green hoses place all of them except the intake hose between the pump frame.
6. Spray gas pump with WD-40
7. Put the green intake hose and the gas pump back in the metal cage.
8. Coil the black freshwater hose and place it back on the cart in the loading dock.
9. Place metal tub on the long cart and pack all other materials into it.

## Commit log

2022-07-27 Add BoM
    [B.xlsx]
2022-07-28 updated bl
    [Bill_of_Materials.xlsx, Pump System Clamp.stl, Pump_System_Extrusion_Bracket_4545.stl]
2022-07-28 Updated BoM
    [Bill_of_Materials.xlsx]
